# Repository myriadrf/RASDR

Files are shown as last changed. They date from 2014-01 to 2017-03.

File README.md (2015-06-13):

# Radio Astronomy Software Defined Receiver (RASDR)

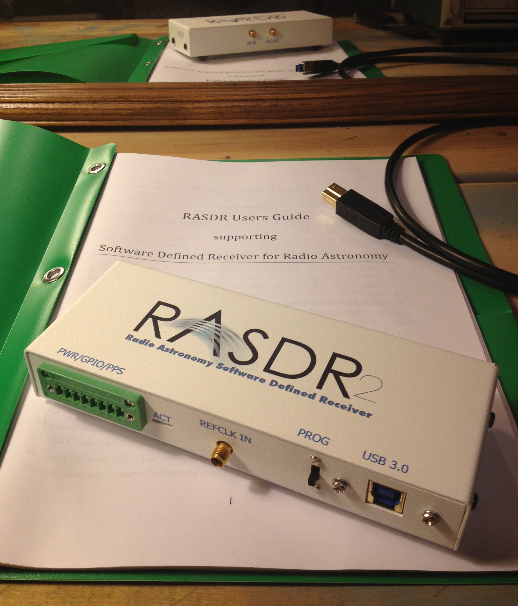
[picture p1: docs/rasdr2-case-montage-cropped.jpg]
RASDR


This project provides access to the hardware designs, firmware, host system drivers and applications for the RASDR project.  RASDR is an Open Hardware project undertaken by members of the Society of Amateur Radio Astronomers (SARA) to develop a low cost, high performance software defined receiver for use by SARA members.  The goal of RASDR is to provide a low cost hardware that enables radio astronomers and educational institutions to perform high quality astronomical measurements.

At the core of this capability is the Lime Microsystems, Ltd. LMS6002D Field Programmable Radio Frequency device.  The device supports tunable RF reception over a wide range (400MHz to 3.8GHz) and high bandwidth (28Mhz).  Through the use of a Host Interface Module, the LMS6002D is connected to a personal computer (PC) over a standard USB link.  Both USB3 and USB2 are supported to enable the widest possible field of use, although full bandwidth of the LMS6002D is only achieved when using USB3.

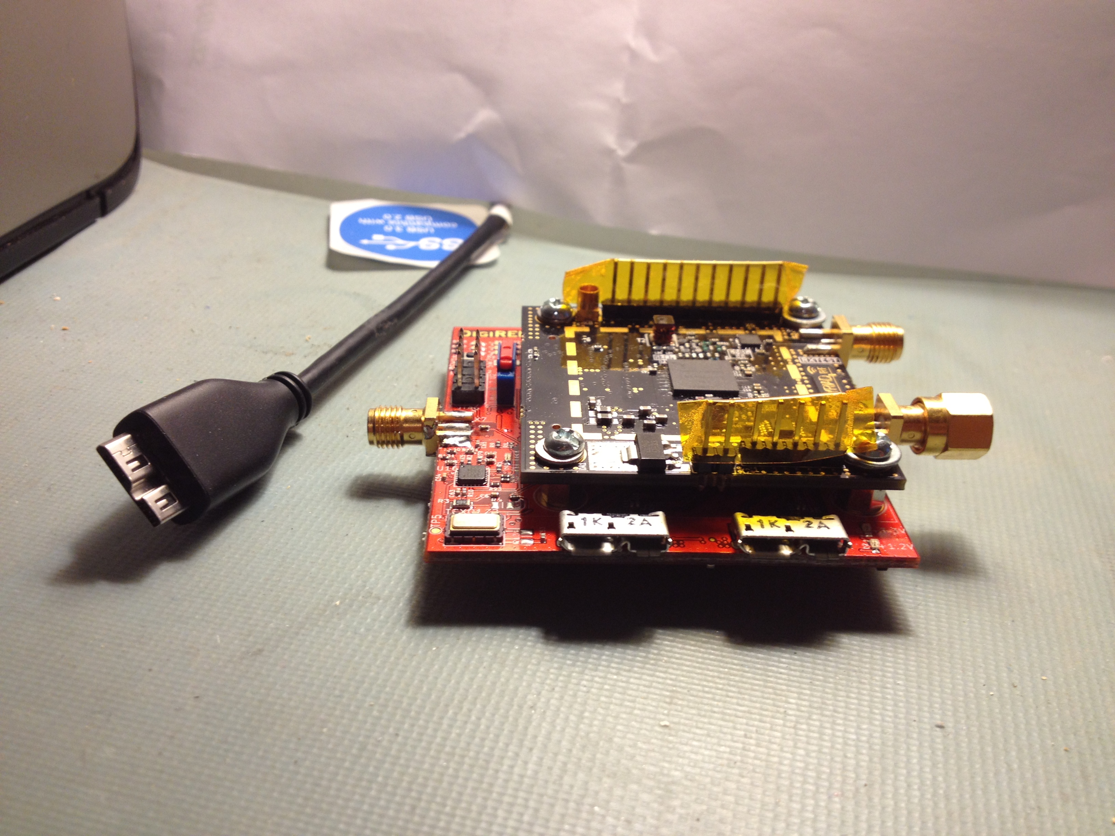
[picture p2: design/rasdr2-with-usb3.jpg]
RASDR-COMPONENTS

*RASDR2 hardware components consisting of DigiRED and MyriadRF modules*

## Device Specifications ##

Radio Astronomy research is dominated by sensitive front-end radio detection and amplification equipment, a wide-bandwidth analog to digital conversion stage, and finally, a digital processing system to extract and present information.  RASDR hardware is designed to provide all these functions in a low size, weight, and power form-factor.

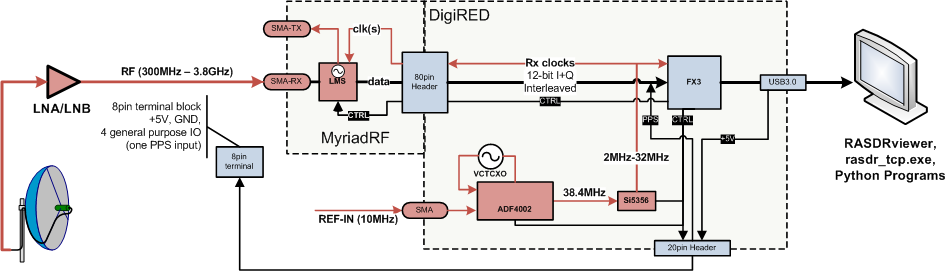
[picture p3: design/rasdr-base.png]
RASDR-DIAGRAM

*RASDR2 block diagram showing basic use case and components*

One RF transceiver chip provides receive functionality.  The transmit section is calibrated to produce a continuous wave (CW) tone that is useful for up/down conversion of signals into the tuning band of the receive section.  Wideband SMA connectors are available to enable reception in the region between 300 MHz to 3.8 GHz with up to 28 MHz of bandwidth at 12 bit I/Q sampling.  The RASDR designs and driver source code are freely available at the RASDR Open Source project, please visit [MyriadRF.org](https://myriadrf.org/) for details.

### Features ###

- Two channel simultaneous receive at max. 28 MHz bandwidth (transmit functions disabled in factory firmware and logic)
- Lime Microsystems, Ltd. FPRF transceiver programmable between 300 MHz to 3.8GHz with 12 bit I/Q sampling and 9 built-in RF Paths.
- Maximum Data Transfer of 160MB/s
- External reference clock input, enabling synchronous operation with test equipment and facility timing signals
- External general purpose I/O (GPIO) port providing 4 3.3V GPIOs and +5V power (1.25W maximum)
- Pulse Per Second (PPS) input on GPIO synchronously sampled and available in the receive data stream
- Power: +5V USB @ 0.75A (3.75W maximum required power)

### Electrical Interface ###

- SuperSpeed USB3 or USB2 data and power.  Max data rates: 160MB/s or 35MB/s respectively.
- SMA receive input, 50ohm, 300MHz to 3.8GHz
- SMA reference input, 50ohm, 10MHz
- SMA transmit output, 50ohm, 300MHz to 3.8GHz

### Physical Specifications ###

- Size:  165mm x 70mm x 32mm (6.5" x 2.75" x 1.25")
- Weight: approx. 653 gram (1lb 7oz.)

## Directory Description ##

- **design** � directory contains high-level design documents and specifications for the RASDR2 module and host APIs. This directory also includes development and testing information.

- **DigiRED** � contains the hardware design files, firmware and information needed to manufacture the various host interfaces modules.  The embedded firmware for the FX3 provides the SuperSpeed USB 3.0 interface and can also be customized for conditional on board processing within the limits of the internal RAM.

- **rfmodule** � contains the hardware design files and information needed to manufacture the MyriadRF module that sits atop the DigiRED.

- **host** � the host directory contains host processor APIs, device drivers and libraries for accessing the RASDR modules via USB. Support is provided for embedded C/C++ development.

## Licensing ##
Unless otherwise specified, all software source files are licensed using the GNU General Public license version 2.  All hardware related designs and source artifacts are licensed under the  �Creative Commons Attribution 3.0 Unported�. To read the details of the license please review "license.html" or visit http://creativecommons.org/licenses/by/3.0/legalcode.

For specific information see the COPYING.MD file(s).

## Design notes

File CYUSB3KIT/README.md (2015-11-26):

# CYPRESS USB 3.0 SuperSpeed Explorer Kit

A Cypress FX3-based interface with general purpose connectivity.

## Contents

This folder contains projects used in debugging RASDR components using the Cypress SuperSpeed Explorer Kit.  This is an inexpensive development board distributed by Cypress Semiconductor, Ltd.

CYUSB3KIT

The hardware can be ordered directly from Cypress; see the information page [here](http://www.cypress.com/documentation/development-kitsboards/cyusb3kit-003-ez-usb-fx3-superspeed-explorer-kit).

## Software

The 'streamer' folder contains a modified version of the Cypress streamer example program that is distributed in the [EZ-USB FX3 Software Development Kit](http://www.cypress.com/documentation/software-and-drivers/ez-usb-fx3-software-development-kit).  It has been updated to compile in Microsoft Visual Studio 2013 Express, to compile outside of the FX3 installation folder, and to allow a queue size of up to 512 transfers.

## Firmware

The 'ssek_emu' folder contains a firmware that is a modified version of the SS Explorer Kit project 'USBBulkSourceSinkLED' .  It has been modified to respond to the RASDR Vendor Command Set, and identify itself as a compatible RASDR device.  The firmware produces representative I/Q data of 'noise' in a replay-buffer manner, at approximately the same rate as a real RASDR device would

The firmware can be loaded to the CYUSB3Kit board by fitting the PMODE jumper J4, resetting the device, and using the CyControl program provided by the RASDR distribution to load the 'ssek_emu.img' to RAM.

To install the firmware into the I2C EEPROM, simply load the 'ssek_emu.img' to I2C.  Upon removing the PMODE jumper and resetting the CYUSB3KIT, the device will function as a RASDR emulator.

## Driver

Use the driver provide by the RASDR distribution for the above firmware(s).  Using the above firmware with the CYUSB3KIT will identify itself as a DigiRED_EMU device.

## Acknowledgement

The RASDR developers wish to thank Cypress Semiconductor, Ltd. for producing the SuperSpeed Explorer Kit, its resulting firmware files.  Inspecting these files has been instrumental in repairing a few long-standing deficiencies in the behavior of RASDR devices and USB3.0.

In addition, the availability of the Kit enables would-be RASDR users to obtain hardware and begin to explore the use of the RASDRviewer and other softwares in advance of obtaining an actual RASDR device which are currently circulating in a loaner program for [Society of Amateur Radio Astronomers](http://www.radio-astronomy.org/) members.

## Licensing

### Software

For details of software licensing please see the associated license.txt files in each folder.

### Firmware

For details of firmware licensing please see the associated license.txt or COPYING file(s) in each folder.

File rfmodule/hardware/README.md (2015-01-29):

# Myriad-RF 1 RF Module version 1

## IMPORTANT!

Previous versions are retained for reference and are not intended for use in manufacturing.

## Changes

Note that r1 and r2 were interim updates and were not manufactured.

### 2014-03-03 r.3

Updated due to obsolete components.

Changed:

#### Schematics updates, pages "Clocks” and  “RF FE":

1. Component DA6 - Obsolete RF switch (PE4210) is changed, to new part PE42422
2. Added capacitor on TX Test track C26=100pF

#### PCB Layout updates

1. New footprint of PE42422 part
2. Rounded RF tracks
3. The GND and power supply vias mask closed (so there is no open vias on board)
4. The board annotation note "Board v.1 r.3" on the bottom layer silkscreen
5. The dimension lines (48 x 46 mm) on Drawings layer

#### BOM updates

1. Manufacturer of the capacitors is to KEMET: Capacitor values: 1.2pF, 1.8pF and 3.9pF
2. Included Board revision line
3. Changed dimensions to 48 x 46 mm
4. Included Drawings layout in list of gerber files
5. Included more report files in report folder

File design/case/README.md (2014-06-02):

# RASDR Case Design Tools

This sub-project generates a case model and manufacturing files for the RASDR project.  RASDR is an Open Hardware project undertaken by members of the Society of Amateur Radio Astronomers (SARA) to develop a low cost, high performance software defined receiver for use by SARA members.  The goal of RASDR is to provide a low cost hardware that enables radio astronomers and educational institutions to perform high quality astronomical measurements.

At the core of this capability is the Object Oriented Mechanics Library ([OOML](http://iearobotics.com/oomlwiki/doku.php)), which is used by the [OOML Case Factory](http://www.thingiverse.com/thing:70838) and custom code to produce the CAD files that are used to generate the STereoLithograpy (STL) files needed to produce a design.

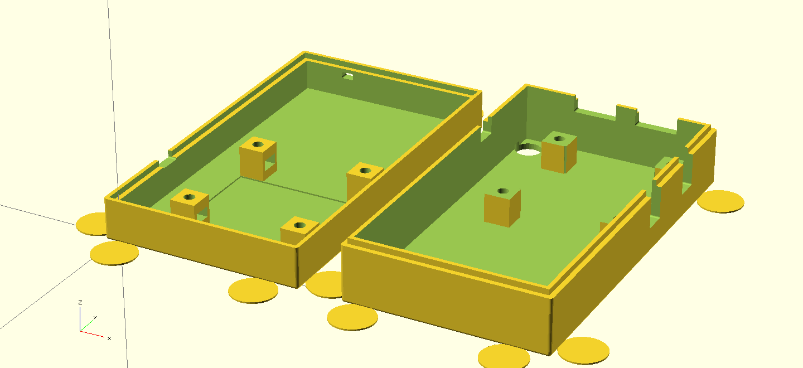
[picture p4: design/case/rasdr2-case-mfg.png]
RASDR

*RASDR2 case design generated using the OOML Case Factory with manufacturing aids*

## Setup of the Tools ##

You will need to setup the OOML and OpenSCAD on your machine.  Here are links:
- [OOML](http://iearobotics.com/oomlwiki/doku.php?id=download:start)
- [OpenSCAD](http://www.openscad.org/)

Forgive me if at this point, I don't have a step-by-step for all platforms.  The above links do a good job.  If you have problems, please send me an email and I'll try to help you out.

## Regenerating the Design ##

Once you have done that, just edit the Makefile to help it find the install location of the library (not needed if you installed into /usr/include/ooml)

Then, simply issue the following commands:

- $ make
- $ ./casefactory

This will produce (at least) the following files:

rasdr-case-bottom.scad
rasdr-case-top.scad
rasdr-case-mfg.scad

The first two are the individual top/bottom parts of the case.  The third is a "manufacturing" version of the case that contains *both* top and bottom parts, as well as 'rafts' to help keep the surfaces from curling.

## Viewing the Design ##

At this point, start OpenSCAD and open one of the above .scad files.  The tool will construct the rendering and you can use the tool to inspect the model from all perspectives, rotate, pan, zoom, etc.

Each time you run the above two commands, you will update the .scad files and OpenSCAD will refresh its rendering.  When you are ready to print the case, you *export* an STL file and send that to your slicer and *happy printing*.

## Licensing ##
These software source files are licensed using the *GNU General Public license version 3*.  This is because the OOML Case Factory is released under this license model.
For specific information see the LICENSE file.

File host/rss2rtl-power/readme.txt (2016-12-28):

Usage: rss2rtl-power.py [options]

 Script to emulate a Radio Sky Spectrograph client application to capture
spectrograph output from a streaming server and write it in an ASCII .csv
format as described by rtl-power.  Two stream protocols are offered: Basic
Radio Sky Spectrograph(http://cygnusa.blogspot.com/2015/07/how-to-talk-to-
radio-sky-spectrograph.html) Binary rtl-power/Extended RSS
Spectrograph(https://github.com/myriadrf/RASDR/issues/16)

Options:
  --version          show program's version number and exit
  -h, --help         show this help message and exit
  -a A, --address=A  Specify the server address; default=localhost
  -p N, --port=N     Specify the port to connect to; default=8888
  -i, --info         Produce information about the connection only; do not
                     receive/parse scans
  -e, --extended     Interpret the extended RSS format
  --iso8601          Emit ISO-8601 Timestamps (YYYY-MM-DDTHH:MM:SS.nnnZ),
                     default=False
  --statistics       Dump statistical information to the stderr in comma-
                     separated-values format, default=False
  -v, --verbose      Verbose
  -q, --quiet        Do not display a connection message on stderr

Examples:

dos> rss2rtl-power.exe > standard.csv

This will start the client, connect to localhost:8888, emit the connection
string and begin reading 'standard' RSS protocol.  It will perform a local
timestamp and write the results to the file standard.csv.

dos> rss2rtl-power.exe -e --statistics > extended.csv

This will start the client, connect to localhost:8888, emit the connection
string and begin reading the 'extended' RSS protocol.  This protocol provides
the timestamp in the packet header and higher precision on the power spectral
density output.  Statistics will be calculated and emitted on the stderr while
the program runs (not in the output file).  The results will be written to the
file 'extended.csv'.

Notes:

The 'standard' RSS protocol is described here:
http://cygnusa.blogspot.com/2015/07/how-to-talk-to-radio-sky-spectrograph.html

The 'extended' RSS protocol is described here:
https://github.com/myriadrf/RASDR/issues/16

If you have python installed, you can also run the program with the python interpreter:

dos> python rss2rtl-power.py > output.csv

Should produce the same result as using the pre-compiled program.

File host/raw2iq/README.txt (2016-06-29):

Convert RASDRstreamer raw stream into a I/Q output

Usage:
dist\x86\raw2iq.exe [OPTIONS]
Where:
  -i, --input-file FILE   Full path to file to be read or - for stdin
  -o, --output-file FILE  Full path to file to be written or - for stdout
  --iq-polarity N         Define starting I/Q polarity level
                            (0=I sample first, 1=Q sample first, default=0)
  --pps-polarity N        Define OTM/PPS polarity level
                            (0=active low, 1=active high, default=0)
  --flag-value HEX        Define FLAGs code for valid data
                            (two bits, default=3)
  --flag-mask HEX         Define FLAGs mask (two bits, default=3)
  -v                      Increment verbosity level
  --verbose N             Define verbosity level (0=quiet, 1=info, 2=trace)
  -h, --help              Print this help

Examples:

dist\x86\raw2iq.exe < RASDRviewer.raw > test.dat
Converts the .raw file to a binary interleaved 16-bit signed I/Q format file.

dist\x86\raw2iq.exe < RASDRviewer.raw -o test.csv
Converts the .raw file to an ASCII 16-bit signed I/Q comma separated file.

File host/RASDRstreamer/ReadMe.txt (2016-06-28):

==============================================================================
    APPLICATION : RASDRstreamer Project
==============================================================================

This project is derived from the CYPRESS FX3 Development Kit project, "C++ Streamer".  It can be used to collect RAW data from a RASDR device.

The Cypress program, "C++ Streamer" was useful for evaluating USB2/USB3 performance of the FX3 chips.  The original program source is provided at:
"C:\Program Files\Cypress\EZ-USB FX3 SDK\1.3\application\cpp\streamer"

I have updated the program to compile with Microsoft Visual Studio Express 2013 for Windows Desktop, to accept the RASDR VID/PID and to build for X86 and X64 windows archicectures.  Additionally, I have added the ability for it to write data out to a file.  The source code to the program is provided at:
https://github.com/myriadrf/RASDR/tree/master/host/RASDRstreamer

To use the Program, perform the following steps:

1) insert RASDR device to a USB2 or USB3 port
2) Load RASDRviewer 1.2.2.2 or RASDRproc, and configure it to the acquisition parameters you wish to use.  { sample rate, samples/frame, bandwidth, gain settings, etc. }
   a. Please note that when using USB2, 10 MS/s is the practical limit
3) Ensure that you are taking data the way you want it by using RASDRviewer to START and STOP capturing samples.
4) Start RASDRstreamer.exe (x86 or x64) and select the RASDR device in the Connected Devices List
   a. This may either be "(0x1D50 - 0x6099) RASDR Radio Astronomy SDR..."
   b. Or it may be "(0x04B4 - 0x00F1) Cypress FX3 USB StreamerExample..." (if you are using the CYFX3KIT hardware for testing)
   c. Select the "BULK IN ..." Endpoint
5) Select the 'Samples/Frame', 'Rate (MHz)' and 'Integration Time (ms)' fields to match what RASDRviewer was set to.
   a. These settings only define the packetization parameters, the actual transfer rate was defind by the RASDRviewer configuration of the LMS6002D chip.
6) Decide you wish to save RAW data or not by ticking the check box
   a. When using USB3 and writing .raw file, you will observe a rate reduction when the in-memory file system buffers fill up.
7) Press START.

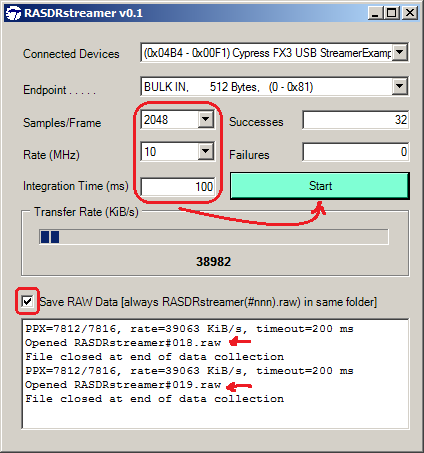
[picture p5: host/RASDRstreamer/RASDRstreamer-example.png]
RASDRstreamer-example

*RASDRstreamer GUI showing steps 4-7 and example progress output*

You will observe successful packets accumulating, the actual transfer rate in KiB/s reported in the GUI.  In the text box below the transfer rate, you will see the packetization parameter and the expected transfer rate based on the selection above.  If you chose to save RAW data, it will also tell you the filename it chose to use.

The program does not overwrite an existing file, rather it adds a '#NNN' suffix to create a unique filename each time.  The files will always have the form 'RASDRstreamer#NNN.raw' as described in the GUI and will always be in the location in the filesystem that the .exe is started from [as of v0.1].

The format of the data are interleaved I and Q 16-bit samples encoded as described in Appendix E of the RASDR User Manual pg. 67-68.  That is, the control bits for I/Q, FIFO flags and PPS are encoded and must be removed in post-processing to interpret the ADC data.  The I/Q streams will also need to be de-interleaved and aligned.  If the HOST PC data acquisition system cannot keep up with the actual data rate (as calculated) then correct interpretation of the I/Q data may require flipping of bits and re-synchronizing to the PPS signal bit.

NOTE:  As per Microsofts documentation:
https://msdn.microsoft.com/en-us/windows-drivers/develop/using_the_microsoft_c_runtime_with_user_mode_drivers_and_apps

The VC re-distributable components are provided with the application file.  They can also be downloaded here:
https://www.microsoft.com/en-us/download/details.aspx?id=40784

==============================================================================
    BUGS
==============================================================================

1) RASDR2 Firmware prior to June 2016 (Device Descriptor BcdDevice="00 03" or earlier) had issues with USB3 operation on certain computers (lower specification) that caused glitches and failed transports.  With Firmware BcdDevice="00 04", this has been *partially mitigated* by eliminating the burst mode when using USB3 SuperSpeed mode.  The change does not eliminate the glitch, but reduces its liklihood considerably.

The workaround is a software close and re-open of the USB device.  For RASDRstreamer, this can be accomplished by restarting the program or stopping the transfer and re-selecting the device, then pressing START.  With version v0.2.1 and later, the program has a compile-time choice to perform a self-restart and continue acquiring buffers.  This seems to work until the firmware gets into a non-recoverable state (see #3) below, which then requires a disconnect/reconnect cycle.

2) v0.1.2 and below of RASDRstreamer has a threading issue in the ::Display() call that leads to random exceptions.  Particularly if there is an early failure in the USB immediately upon pressing the START button.

3) If you get 'Xfer request rejected. NTSTATUS = c0000001' when trying to START, this means that the firmware has entered an invalid state, and the device must be disconnected and reconnected.  (The Firmware BcdDevice="00 04" is only *partially mitigated*) 
 
==============================================================================
    CHANGELOG
==============================================================================

v0.2.2 - Bugfix

  Add workaround for NULL endpoint at Start
  Fix bug that caused Device selection to be left disabled upon a failure at start.

v0.2.1 - First release with restart capability

  Add (configurable) code to re-initialize the USB device when a transfer failure is detected
  Refactor management of the USBDevice and EndPt pointer to reduce interdependent references
  (some whitespace changes due to the microsoft editor)

v0.2.0 - Unreleased

  Refactor buffers in XferLoop() to be conducive to restart operation
  Keep success/failure count persistent across XferLoop() starts/stops

v0.1.3 - Unreleased

  Add queued string output to prevent crashes
  Add temporary workaround 'CheckForIllegalCrossThreadCalls=false' for calling UI components from thread functions

<rant>Why does *every* example software have such bad UI thread issues?  Its crushing how much code is written like this.  It works for simple cases, and then as soon as you start to extend it...  boom, crash, game over.  Its such a waste of time.  You were much better off starting from scratch.  But then...  you will have invested so much time in the code that any rational human being will want to get some compensation for it, and you will close the source and keep it secret.  Well, I am not rational, so I hope that my (insignificant) efforts at repairing these will help some poor soul stuck with the same problems in the code they have to deal with.</rant>

v0.1.2 - Unreleased

  Add vertical scrollbar to diagnostic output
  Fix bug not using 'rb' when writing .raw files that leads to files getting premature EOF

v0.1.1 - First Public Distribution

  Track when transfer rate is not close to what is expected
  Color the transfer rate bar if the expected/actual data rate differs by more than 3% and 10%
  Fix bug when closing if raw output file is not opened

v0.1 - First Source Code Release

  Evaluates expected/actual data rate received, handles (recoverable) USB3 glitches gracefully.  Saves .raw files not overwriting the previous sequence number if it exists.

==============================================================================
    FILE SUMMARY
==============================================================================

This is a summary of what you will find in each of the files that make up the Streams application which uses cypress C++ library CyAPI.lib.

RASDRstreamer.vcproj/.vcxproj
    This is the main project file for VC++ projects generated using an Application Wizard. 
    It contains information about the version of Visual C++ that generated the file, and 
    information about the platforms, configurations, and project features selected with the
    Application Wizard.

RASDRstreamer.cpp
    This is the main application source file (boilerplate).

RASDRstreamer.h
    Contains the implementation of the program, according to .NET style.

AssemblyInfo.cpp
    Contains custom attributes for modifying assembly metadata.

Other standard files:

StdAfx.h, StdAfx.cpp
    These files are used to build a precompiled header (PCH) file
    named Win32.pch and a precompiled types file named StdAfx.obj.

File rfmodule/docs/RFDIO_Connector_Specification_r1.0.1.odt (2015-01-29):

RFDIO Connector

Specification

v1.0

Copyright 2014 Lime Microsystems Ltd

CC BY 3.0

Contents

Table of Figures

Figure 1. RFDIO connectors 3

Figure 2. Recommended PCB footprint 5

Figure 3. MyriadRF card mechanical coordinates (Top view) 5

The information contained in this document is subject to change without prior notice. No responsibility for its use, nor for infringement of patents or other rights of third parties is assumed.

The information contained in this document is subject to change without prior notice. No responsibility for its use, nor for infringement of patents or other rights of third parties is assumed.

# General Description

The Myriad-RF Radio Frequency Digital Input Output (RFDIO) connector specification defines the electrical and mechanical properties of a high speed card interface for Field Programmable Gate Array (FPGA) based carrier boards. This specification ensures interoperability between carrier (mother) boards and add-on (daughter) RF cards.

The connector is designed to meet the IEEE802.3ap backplane link to meet 10G Ethernet compliant signal channels.

# Mechanical Specifications

The connector is based on the Hirose 0.5 mm pitch, 80 positions, surface-mount connector. The part numbers are:

The female part number is FX10A-80S/8-SV, to be assembled on the motherboard. The male part number is FX10A-80P/8-SV1, and is to be used by the daughterboard. A typical example of use for an RF application is an Altera FPGA motherboard, using a Myriad-RF daughterboard. This example with be used in the document for clarity.

Figure 1 shows the connectors in 3-D view.

Figure 1. RFDIO connectors

Figure 2 shows the recommended land pattern (Metal Mask) connector dimensions.

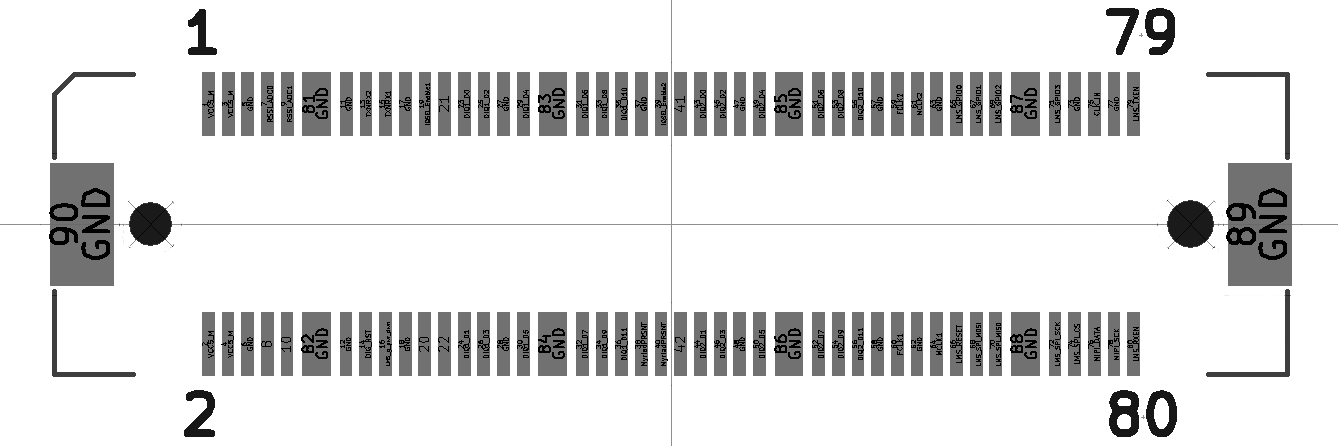
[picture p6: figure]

1.6

0.3

0.7

0.5

0.75

3.05

3.1

1.6

13.2

14.95

1.1 NPTH

1.2 NPTH

Figure 2. Recommended PCB footprint

A footprint for the open source EDA software, KiCad, is available via the database provided by the Myriad-RF Component Libraries project (https://myriadrf.org/projects/component-libraries/).

Figure 3 shows the dimensions of the Myriad-RF 1 daughterboard with the Hirose connector.

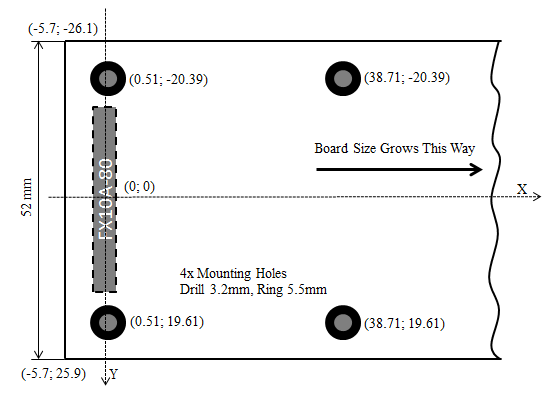
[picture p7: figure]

Figure 3. Myriad-RF card mechanical coordinates (Top view)

# Electrical Specifications

## Power

The carrier board must provide +5V (1.5A) DC to the RF card through the RFDIO connector. The maximum current via the Hirose connector is 0.3A per pin. To achieve the 1.5A specification, a number of defined supply and ground pins must be used. These are:

+5V: Pin 1, 2, 3, 4, 8 & 10.

GND: Pin 5, 6, 11, 12, 17, 18, 27, 28, 37, 38, 47, 48, 57, 58, 62, 63, 73, 77, 81, 82, 83, 84, 85, 86, 87, 88, 89 & 90

## CMOS Signals

The CMOS class pins are intended to connect directly to pins that support LVTTL compatible single-ended I/O standards such as 3.3-V LVTTL/LVCMOS or 2.5-V LVTTL/LVCMOS.

All CMOS class pins must support bidirectional operation.

Signals between the host FPGA device and HSMC connector are intended to be D/C coupled.

## Bus Widths

Daughterboards must be designed to support the full specified bus widths. This will guarantee interoperability with the greatest number of RF cards.

## Termination

Tracks must have 50 Ω single-ended impedances. An optimum design will be obtained if the host FPGA supports driver strength control where 50 Ω output impedances can be selected. This output impedance will match the characteristic impedance of the tracks themselves. For long track lengths or heavy loads, drive strength may be increased as necessary until optimal signal integrity is achieved for the specific carrier board or RF card combination. When impedance control is not possible, it is recommended to place series resistors on each line of the host board to allow for tuning through resistor value changes. Default resistors should be a nominal 0 Ω since signal direction cannot be assumed on a carrier board and higher value resistors found near a receiver can significantly degrade signal integrity.

## Pinout

The RFDIO connector has a total of 90 pins, including 54 digital signals pins, 6 power pins, 2 analog pins and 28 ground pins.

Table 1 (Part 1 of 2). RFDIO connector’s pinout

Pin Nr | Function | Description | Pin Nr | Function | Description
1 | 5V | Power | 2 | 5V | Power
3 | 5V | Power | 4 | 5V | Power
5 | GND | Power | 6 | GND | Power
7 | RSSI output | analog | 8 | 5V | Power
9 | RSSI output | analog | 10 | 5V | Power
81 | GND | Power | 82 | GND | Power
11 | GND | Power | 12 | GND | Power
13 | TXNRX2 | CMOS IN | 14 | GPIO5 | CMOS IO
15 | TXNRX1 | CMOS IN | 16 | G_PWR_DWN | CMOS IN
17 | GND | Power | 18 | GND | Power
19 | ENABLE_IQSEL1 | CMOS IN | 20 | GPIO6 | CMOS IO
21 | SPI_EN_BRD | CMOS IN | 22 | GPIO7 | CMOS IO
23 | DIQ1_D0 | CMOS IO | 24 | DIQ1_D1 | CMOS IO
25 | DIQ1_D2 | CMOS IO | 26 | DIQ1_D3 | CMOS IO
27 | GND | Power | 28 | GND | Power
29 | DIQ1_D4 | CMOS IO | 30 | DIQ1_D5 | CMOS IO
83 | GND | Power | 84 | GND | Power
31 | DIQ1_D6 | CMOS IO | 32 | DIQ1_D7 | CMOS IO
33 | DIQ1_D8 | CMOS IO | 34 | DIQ1_D9 | CMOS IO
35 | DIQ1_D10 | CMOS IO | 36 | DIQ1_D11 | CMOS IO
37 | GND | Power | 38 | GND | Power
39 | ENABLE_IQSEL2 | CMOS IN | 40 | BRDPRSNT | Board present, connects to GND on RF card
41 | GPIO4 | CMOS IO | 42 | VIO | Digital IOs supply
43 | DIQ2_D0 | CMOS IO | 44 | DIQ2_D1 | CMOS IO
45 | DIQ2_D2 | CMOS IO | 46 | DIQ2_D3 | CMOS IO
47 | GND | Power | 48 | GND | Power
49 | DIQ2_D4 | CMOS IO | 50 | DIQ2_D5 | CMOS IO
85 | GND | Power | 86 | GND | Power
51 | DIQ2_D6 | CMOS IO | 52 | DIQ2_D7 | CMOS IO
53 | DIQ2_D8 | CMOS IO | 54 | DIQ2_D9 | CMOS IO
55 | DIQ2_D10 | CMOS IO | 56 | DIQ2_D11 | CMOS IO
Table 1 (Part 2 of 2). RFDIO connector’s pinout
Pin Nr | Function | Description | Pin Nr | Function | Description
57 | GND | Power | 58 | GND | Power
59 | FCLK2 | CMOS CLK in | 60 | FCLK1 | CMOS CLK in
61 | MCLK2 | CMOS CLK out | 62 | GND | Power
63 | GND | Power | 64 | MCLK1 | CMOS CLK out
65 | GPIO0 | CMOS IN | 66 | RESET | CMOS IN
67 | GPIO1 | CMOS IN | 68 | SPI_MOSI | CMOS IN
69 | GPIO2 | CMOS IN | 70 | SPI_MISO | CMOS OUT
87 | GND | Power | 88 | GND | Power
71 | GPIO3 | CMOS IN | 72 | SPI_CLK | CMOS IN
73 | GND | Power | 74 | SPI_EN_LMS | CMOS IN
75 | CLK_IN | CMOS Reference CLK input for RF card | 76 | MIPI_SDA | CMOS IO
77 | GND | Power | 78 | MIPI_SCL | CMOS IN
79 | TXEN | CMOS IN | 80 | RXEN | CMOS IN
89 | GND | Power | 90 | GND | Power

*for complete signals description and timing diagrams refer to LMS6002D (http://www.limemicro.com/download/LMS6002Dr2-DataSheet-1.2r0.pdf) or LMS7002M (http://www.limemicro.com/download/LMS7002M-DataSheet%202.0r1%20Preliminary.pdf) datasheet

Myriad-RFRFDIO Connector Specification

Rev: 1.0.1 The information contained in this document is subject to change without prior notice. No responsibility for its use, nor for infringement of patents or other rights of third parties is assumed. Rev: 1.0.1 Last modified: 12/16/2014 The information contained in this document is subject to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

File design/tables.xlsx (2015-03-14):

DigiRED R50,52,56 | MyriadRF R95 | SPI_SSN_Rx pullup | SPI_SSN_Rx pulldn | Jumper on J2 (RX) | Press SW2 (RX) | Power On | Boot Behavior | Voltage at R115 | Current thru R115 | Notes
YES | YES | N/C | N/C | NO | X | X | Bootloader | N/A | N/A
YES | YES | N/C | N/C | YES | YES | NO | Bootloader | N/A | N/A
YES | YES | N/C | N/C | YES | NO | YES | Load SPI Flash Program | N/A | N/A
YES | NO | N/C | N/C | NO | X | X | Bootloader | N/A | N/A
YES | NO | N/C | N/C | YES | YES | NO | Bootloader | N/A | N/A
YES | NO | N/C | N/C | YES | NO | YES | Bootloader | N/A | N/A
NO | N/C | N/C | N/C | NO | X | X | Bootloader | N/A | N/A | MyriadRF board is not attached
NO | N/C | N/C | N/C | YES | YES | NO | Load SPI Flash Program | N/A | N/A | MyriadRF board is not attached
NO | N/C | N/C | N/C | YES | NO | YES | Load SPI Flash Program | N/A | N/A | MyriadRF board is not attached
NO | NO | N/C | N/C | X | X | X | Bootloader | N/A | N/A
NO | NO | 100 ohm | NO | YES | NO | YES | Bootloader | 3.29V | 0 mA
NO | NO | 100 ohm | NO | YES | YES | NO | Bootloader | 3.29V | 0 mA
NO | NO | NO | 100 ohm | YES | NO | YES | Load SPI Flash Program | 2.7V | 27 mA
NO | NO | NO | 100 ohm | YES | YES | NO | Bootloader | 0.0V | 0 mA
NO | NO | NO | NO | YES | NO | YES | Bootloader | 2.6V | N/A
NO | NO | NO | NO | YES | YES | NO | Bootloader | 2.6V | N/A
NO | NO | 2.2K ohm | NO | YES | NO | YES | Bootloader | 3.29V | 0 mA
NO | NO | 2.2K ohm | NO | YES | YES | NO | Bootloader | 3.29V | 0 mA
NO | NO | NO | 2.2K ohm | YES | NO | YES | Load SPI Flash Program | 3.26V | 1.5 mA
NO | NO | NO | 2.2K ohm | YES | YES | NO | Bootloader | 0.1V | 45 uA
NO | N/C | 2.2K ohm | NO | YES | NO | YES | Load SPI Flash Program | 3.29V | 0 mA | MyriadRF board is not attached
NO | N/C | 2.2K ohm | NO | YES | YES | NO | Load SPI Flash Program | 3.29V | 0 mA | MyriadRF board is not attached
NO | N/C | NO | 2.2K ohm | YES | NO | YES | Load SPI Flash Program | 3.26V | 1.5 mA | MyriadRF board is not attached
NO | N/C | NO | 2.2K ohm | YES | YES | NO | Load SPI Flash Program | 3.26V | 1.5 mA | MyriadRF board is not attached

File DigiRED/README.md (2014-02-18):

# DigiRED USB 3.0 Interface Module 

A Cypress FX3-based interface for the Myriad-RF 1 module.

## Contents

### Hardware design

The directory structure for the hardware design is as follows:

      hardware/<version>/
          BOM/                   - bill of materials spreadsheet
          Gerbers/               - Gerber CAM files
          KiCAD/                 - KiCAD schematic and layout files
          Manufacturing/         - Additional manufacturing information
          PDF/                   - Schematic and layout PDFs
          Reports/               - DRC, ERC and drill reports

## Firmware

FX3 controller firmware.

      firmware/
          bin/                   - binary releases
          src/                   - source code

## Driver

Windows drivers for the DigiRED Module

      driver/
          digired-windows.zip    - Windows Drivers for DigiRED

## Licensing

### Hardware

The hardware design is licensed under a Creative Commons Attribution 3.0 Unported licence.

### Firmware

For details of firmware licensing please see the associated COPYING file(s).

### Driver

For details of driver files licensing please see the license.txt in the driver/

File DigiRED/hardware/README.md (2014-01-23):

## DigiRED Hardware Designs ##
This directory contains the hardware source artifacts for the DigiRED host interface module.  

## Directory Structure ##
The directory is organized into the various published hardware revisions: v1r3(prototype), etc...

----------

## Designs / Source Artifacts Licensing ##
All hardware source artifacts contained within this directory are licensed under the “Creative Commons Attribution 3.0 Unported”.  To read the details of the license please review "COPYING" or visit [http://creativecommons.org/licenses/by/3.0/legalcode.](http://creativecommons.org/licenses/by/3.0/legalcode.)

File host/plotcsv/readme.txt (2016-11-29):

usage: plotcsv.py [-h] [--version] [-v | -q] [-a N] [-b PATH] [-c] [-d CHAR]
                  [-e] [-k CONST] [-l] [-i] [--statistics PATH] [--debug] [-g]
                  [-s N] [--fcenter FC] [--hold] [--bplot] [--ptype TYPE]
                  [--atype TYPE] [--format X.Y.Z]
                  [file [file ...]]

Post-Process RASDRviewer/RASDRproc spectrum data output files

positional arguments:
  file

optional arguments:
  -h, --help            show this help message and exit
  --version             show program's version number and exit
  -v, --verbose         Turn on verbose output
  -q, --quiet           Suppress progress messages
  -a N, --average N     Specify the number of spectra to average for each plot
  -b PATH, --background PATH
                        Specify how to perform background subtraction;if the
                        word automatic is used, then the background will be
                        takenfrom the average of all lines in the file.
                        Otherwise, it is takenas a file to process. The file
                        must have the same frequency plan as the foreground
                        file.
  -c, --cancel-dc       Cancel out component at frequency bin for 0Hz
  -d CHAR, --delimiter CHAR
                        Specify the delimiter character to use"
  -e, --localtime       Indicate that .csv file has timestamps in
                        RASDRviewer's "LocalTime" format
  -k CONST, --calibration CONST
                        Specify the calibration constant for the system;
                        0.0=uncal
  -l, --line            Perform line-by-line processing instead of loading
                        entire file(s); NOTE: much slower but tolerates low
                        memory better.
  -i, --info            Produce information about a file only; do not generate
                        any plots
  --statistics PATH     Dump statistical information to a file in comma-
                        separated-values format
  --debug               Drop into ipython shell at predefined point(s) to
                        debug the script
  -g, --gui             Create interactive PLOTS
  -s N, --smooth N      Smooth final plot using a sliding window of N points
  --fcenter FC          Define the offset for the center frequency in Hz
  --hold                Perform a maximum value HOLD during averaging and plot
                        it as a second line
  --bplot               If using background file, choose whether to plot the
                        background reference in a difffert color
  --ptype TYPE          Control plot vertical scale (linear or log)
  --atype TYPE          Control averaging method (linear or log)
  --format X.Y.Z        Specify the RASDRviewer .csv output format to
                        interpret

NOTES:

Edit the 'go.bat' provided to assign the path to the file and any needed options.  Then double-click the go.bat file.

If you have python installed, you can also run the program with the python interpreter:

dos> python plotcsv.py FFTOut-2msps-500avg-srh77ca.csv -a 120

Should produce the same result as using the pre-compiled program.

Several versions of RASDRviewer had produced different header formats that
need to be parsed differently.  The --format option allows you to specify
this if you are dealing with older data files.  Currently valid options are:
1.0.4, 1.1.1, 1.2.2 (current)

The file 'environment.yml' provides an easy way to generate a python virtual environment that has the needed dependencies.  Using Anaconda, execute:

$ conda env create -f environment.yml
$ source activate rasdr
-or-
dos> activate rasdr

See: https://docs.continuum.io/anaconda/install.html
See also: http://conda.pydata.org/docs/using/envs.html#use-environment-from-file

BUGS:

1) the cancel DC option isnt effective as it seems the highest energy is 2 bins away from actual Frequency 0
2) The file formats need to be described
3) The 'append' feature in RASDRviewer that adds a new frequency header to the same file is not supported correctlyUsage: plotcsv.py <filename.csv> [options]

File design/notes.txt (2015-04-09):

To produce GERBER manufacturing files from KICAD (pcbnew)

1) Choose File->Plot
2) select Plot Format 'Gerber', output directory '../Gerbers/', select layers
   a. see 'digired-gerber-files-output.png'
   b. press 'PLOT'
3) in the same window, press 'Generate Drill File'
   a. see 'digired-drill-files-output.png'
   b. press 'Drill File'
   c. press 'Map File'
   d. press 'Report File'
      1. choose ../Reports/DigiRED_v1.0-drl.rpt'

To compare Gerber files

1) download and install 'gerbv'
   a. see http://gerbv.geda-project.org/
2) Load a full set of gerber files, and set the rendering color to WHITE
   a. turn all layers OFF (to prevent re-rendering while colors are changed)
   b. select each layer, press F6
   c. set the R=255, G=255, B=255
3) Load the comparison set of gerber files, and set the rending color to WHITE
   a. see 2) above
   b. alternatively, you can edit the project file and set each layer color to #(65535 65535 65535)
4) Fit all layers into the rendering window
   a. Select Layer->All On
   b. View->Rendering->Fast
   c. View->Best Fit
5) Prepare to compare
   a. Select Layer->All Off
   b. View->Rendering->Fast(XOR)
6) select pairs of matching layers to enable.  Each pair you enable will be rendered in XOR and differences highlighted.  if there are no differences, the resulting image will be black.

To translate Gerber files to PDF:

1) download 'gerber2pdf.py'
   a. see http://pages.swcp.com/~jchavez/gerber2pdf.html
2) ensure dependencies are satisfied
   a. dos> pip install plex
   b. dos> pip install reportlab
3) python gerber2pdf.py
   a. follow the prompts.  Choose 'fit to page=1' to get any output
   b. gerber.pdf is produced in the same folder as the first gerber file in the list

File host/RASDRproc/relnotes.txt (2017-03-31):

RASDRproc v0.2.5.4 -  Jan 22, 2017
==================================

RASDRproc.exe is the open-source version of the RASDR device setup and data collection program
RASDRproc_d.exe is a debug version that opens a DOS console which writes diagnostic data out

The program is able to configure RASDR2 and RASDR3 devices, set sample rates and receiver parameters.  It can optionally also display received data in time and frequency domain, I vs Q and total power.  Data collected may be saved to ASCII output files for further analysis and post-processing.

System Requirements:

1. Windows (XP or later) machine.  Dual core machines will work but a quad (or larger) core system is recommended.
2. Lime Microsystems/Myriad RF - DigiRed board with Myriad RF board ("RASDR2").
3. USB 2 or USB 3 port.
4. SARA "RASDR Radio Astronomy SDR Rx Interface" driver.

Usage:

Connect a RASDR2 device to the USB port of your computer (see the RASDR user manual for details on assigning the driver).  Double-click either RASDRproc or RASDRproc_d and wait for it to configure the device.  If you see non-zero values for "chip: rev: mask:" in the lower-left corner of the screen, it has connected to the RASDR device successfully.  Otherwise, you may still use the GUI functions to setup the configuration file.

At this point, you may press 'Start Acquisition' and observe the data collection.

When you close the program, the last set of parameters used will be written to the "RASDR.cfg" file for use next time.  RASDRproc produces annotated configuration files whose settings are described in the file itself.  It is compatible with the (un-annotated) ASCII configuration files used by RASDRviewer 1.2.2.2 and BELOW.

DC Offset Correction:

RASDRproc employs *post* acquisition DC Offset Correction.  The calibration procedure is as follows:

1) Setup the desired acquisition parameters and start data collection.  While collecting data, connect a 50ohm load to the RX of the receiver.  With v0.2.3.7+, you may also select the RX input to 'disconnect'.  While this is not a 50ohm load (rather a High-Z) it can still be useful for adjusting the DC offset. 

2) From the 'Performance Parameters' menu, select 'Tuning Parameters'.  This brings up a pop-up window where an I and Q offset is able to be entered.  While data is being collected, press the 'Use Current Averages' and observe that the values are updated. Then, press 'OK Accept Values' and see that the DC offset correction is applied.

The calibration values are saved along with the other parameters in the RASDR.cfg file.

If necessary, repeat the above procedure to compute new offsets.  Typically, it has not been seen that the offset needs to be corrected continuously, but the offset IS different each time the RASDR2 device is powered up and it does depend on what antenna system and front end electronics are connected to the RASDR RX port, as well as the sampling rate and gain settings.

NEW with v0.2.3.4:  The DC calibration can be made from the front panel.  A measure of the difference between ideal is calculated and displayed continuously according to the Mean-Square-Error formula:

MSE = ((DCOffsetI - avgI)^2 + (DCOffsetQ - avgQ)^2) / 2.0

CHANGED with v0.2.3.8:  Added a measure of the %-difference from the maximum ADC value that the DC offset is set to.  The background color of the skew metric is now as follows:

If the PERCENT is < 5.0 the display will be gray
If the PERCENT is 5.0 < 10.0, the display will be yellow
If the PERCENT is > 10.0, the display will be red

The option to do automatic (continuous) DC offset calibration (that was the only option in RASDRviewer 1.2.2.2 and BELOW) is restored with a check-box in RASDRproc v0.2.3.4 and above.

NOTE: there is a DC offset adjustment that is performed on the LMS chip as part of tuning, but currently it is an open-loop procedure that is does not produce optimal result.  Future revisions may address this issue.

Auto Restart:

RASDR2 devices when used in USB3 on marginal machines exhibit a stall acquiring data.  It has been shown that if data acquisition is stopped, then started dataflow may recover (but not always).  In those cases, the driver must be closed and re-opened, and then dataflow recovers.  This version of RASDRproc implements a detection and mitigation for this condition.  It is enabled by checking the 'Auto Restart' tick box in the upper right corner near the frame rate display.

In addition, this version annotates the data rate and frame rate display with a comparision to the expected rates and uses a RED or YELLOW background if the program is not keeping up.  The thresholds are fixed at compile time at the moment.

With v0.2.3.6, some aspects of this have changed.  Users have reported random application crashes and these appear to be related to thread-safety issues which are endemic in the code architecture.  A small amount of safety w/r/t the access to the endpoint data structures and the CyUSB library was put into place, and it seems to have a positive effect upon the liklihood of an application crash when stopping.  I have a low-spec development system in which USB3 operation is extremely marginal, calling for frequent resets of the USB device.

Gain, Bandwidth and LNA Selection:

With v0.2.3.7, some aspects of this have changed.  Changing gain values for the VGA and LNA as well as the LPF filter bandwidth now takes place immediately upon selection.  I.e. it is not required to 'Apply' which would cause an acquisition stop, configure and acquisition start cycle.  The only setting that requires an 'Apply' is the changing of the 'RF Ctr Freq' (and that is only due to more complex GUI issues than any actual restriction in the LMS6002D).  The 'Apply' button has been moved and renamed to be near the entry field.

Further, with v0.2.3.7, the ability to select which LNA port is active on the LMS6002D chip is available.  However, testing has shown that LNA1 is the only viable port; LNA3 does not appear to provide a useful response in tests conducted at 408MHz (even though it *should*).  Additionally, the RX->LNA switching that is available on the DigiRed board is now exposed.  This means that the user can disconnect the LMS6002D from the RX input to measure internal system behavior.  NOTE: it does not provide a 50ohm input to the LNA, rather it provides a Hi-Z.  This is the way that the circuit is wired on the DigiRed, and identifies an area of inprovement in the next design.

The bottom row status is updated to provide additional details on the specification of the input selected.

Radio Sky Spectrograph Integration:

This version supports a TCP/IP connection to allow Radio Sky Spectrograph to manage the display of a waterfall.  The protocol is described here:
http://cygnusa.blogspot.com/2015/07/how-to-talk-to-radio-sky-spectrograph.html

in RASDRproc the TCP/IP server, if enabled, will be active during periods of active acquisition (after pressing 'Start Acquisition').  In RSS, you tell it to use the 'RTL Dongle Receiver' under the Radio menu.  The connection is established by RSS when you press 'Start' on its GUI.  If you change certain parameters in RASDRproc or otherwise affect the frequency plan, the connection will disconnect and you can re-start by 'Start' on the RSS screen.  It seems to be pretty robust.  Please do make sure that RASDRproc RSS output is enabled and acquiring data *first* before pressing 'Start' on RSS.  Otherwise, it may take some time for it to timeout.

The RSS control panel (in RASDRproc Define Output->Setup RSS Output menu) has several tunable parameters:

- Channel Offset
- Channel Gain
- Channel Bias

These affect the calculation of the spectrum output as follows:  S[n] = (( s[n] + offset ) * gain ) + bias

- Minimum Value (clip)
- Maximum value (clip)

These will enforce the spectral outputs to limit values

- Frequency Offset

This can be used if you are using an upconverter to provide the correct offset frequency so that RSS will display the actual RF frequency instead of the IF frequency that the RASDR unit is tuned to.  NOTE: by rights, this is needed to be known by RASDRproc itself, but so far it was not implemented that way.  In the future this control may move to a different place, but for now it is listed here with the RSS stuff.

There was a regression in v0.2.3.4 in which the RSS control panel settings became unavailable.  This was corrected in v0.2.3.5 (and hopefully from now on). 

NEW with v0.2.5.2:  The "Extended RSS" protocol is implemented as described here:
https://github.com/myriadrf/RASDR/issues/16

In a nutshell, the RASDRproc program acts as a TCP server and listens for a connection on the port defined by the 'Setup RSS Output' as described above.  Configure your external program to connect to this IP:PORT combination.  Upon a connection, RASDRproc accepts the connection and sends an 1024-byte ASCII string as a response.  The response will be key value combinations separated by the "|" character.

The following keys will be provided:
    [CenterFrequencyHertz] The tuned center frequency in Hz
    [BandwidthHertz] The bandwidth of the observation in Hz
    [OffsetHertz] The offset frequency (in case an LNB or up/down converter is used with the receiver)
    [NumberOfChannels] The number of frequency bins that will be provided for each scan line

The following keys may be provided:
    [IntegrationTimeSec] The amount of integration in seconds that will be used for each scan line
    [GainDb] The total amount of receiver gain used
    [NotesString] An ASCII string provided by the program to describe the observation (excluding the "|" character).

For example:
    CenterFrequencyHertz 21000000|BandwidthHertz 5000000|OffsetHertz 0|NumberOfChannels 2048|

This would tell your program that the center frequency of the observation is 21 MHz. The bandwidth is 5 MHz, so the display will run from 21 + 2.5 to 21 - 2.5 MHz, or 18.5 MHz to 23.5 MHz. There is no offset so no frequency converter is used. Finally, NumberOfChannels denotes the number of channels that will be reported for each of the spectrum scans. There is no predefined limit on the number of channels, but the number is limited to a 4-byte unsigned integer. The connection block will be a fixed-size of 1024 bytes. Each of these parameters is separated by the pipe symbol "|". The parameter string will end with a CRLF. There may be trailing NUL to complete the 1024-byte connection block description.

Following this, a constant stream of binary data will be provided. It is not necessary to interpret the connection block (above) as the binary stream will self-describe itself. It will consist of the following binary data elements (equivalent to a binary-version of the rtl-power specification) ***in Network Byte Order***:
    [timestamp] IEEE-754 8-byte double representing the seconds since January 1, 1970 (the Unix Epoch)
    [hz_low] IEEE-754 4-byte float representing the center frequency of the lowest frequency bin
    [hz_high] IEEE-754 4-byte float representing the center frequency of the highest frequency bin
    [hz_step] IEEE-754 4-byte float representing the difference between two adjacent frequency bins
    [samples] A 4-byte unsigned integer representing the number of samples used to integrate each frequency bin
    [channels] A 4-byte unsigned integer representing the number of frequency bins to follow
    [db-values] IEEE-754 4-byte float * channels (as given in the header above)

At the moment, as with the Radio-Sky-Spectrograph version, any changes to the acquisition parameters will close the socket, requiring a re-connection.  Subsequent edits will eliminate this need and simply update the stream header dynamically.  If new metadata is desired, disconnect and re-connect to obtain it.

In v0.2.5.4, a bug was fixed in the "Extended RSS" protocol:  The extended RSS protocol is intended to write frequency values from low frequency to high frequency, in order to match the rtl-power format.  Prior to this, it was writing values from high to low frequency like the standard RSS protocol requires.  Also, the timestamping code was updated slightly to propagate it through the buffers.  A future release will introduce a reworked buffer and thread management code.

Background Subtraction:

RASDRproc has had the ability to perform live background subtraction on incoming spectral data.  However, this capability was not fully fleshed out until v0.2.3.8, when several adjustments were made including the exposure of the configuration settings to the Tuning Parameters dialog.

To access the controls, from the 'Performance Parameters' menu, select 'Tuning Parameters'.  This brings up a pop-up window and there are two sections that affect the background subtraction:  'Spectral Averaging' and 'Spectral Background Subtraction'.  Both of these are dynamic in that they can be applied while data collection is active.

>> Spectral Averaging

The two controls here are 'Unlimited Averaging' and 'Reference to ADC Full Scale'.  Both of these features are not yet implemented.

>> Spectral Background Subtraction

In this section there are the following controls:

- Enable

This is used to activate the subtraction of a background level present at the time that the 'SetPwrRef' button is pressed on the main panel.  For testing convenience, a button 'Set Reference' is also provided on the pop-up window to allow adjustments while viewing the response on the main panel.  If this box is checked, then the spectral plot will will display the result of this equasion:

PWR[f] = 10 * log10( (AVG(I[f]^2 + Q[f]^2) - REF[f]) * G )

Where I[f], Q[f] are the normalized FFT outputs.  G is the 'Integration Gain' which is adjustable on the panel.  REF[f] is obtained at the time the 'SetPwrRef' or 'Set Reference' buttons are pressed.  It is computed according to the method control described below.

Please note, that the code does not perform the SQRT of the I,Q data as part of the averaging.  It incorporates the SQRT by using a 10* instead of 20* for the power spectral density calculation.

Also note, the current version of RASDRproc operates as if a rectangular window is applied to the time domain data prior to computing the FFT.  I.e. no windowing function is applied and no overlap of the FFT samples are performed.  Future versions may address this issue.

- Visible

This control determines whether or not the in-use background level is displayed or not.  If ticked, the current background waveform will be overlaid on the spectral plot in green.

- Method

This drop-down box determines the algorithm used to compute the REF[f] vector.  There are four possible choices, described below:

    Mean:  This computes the mean value of the AVG(I[f]^2 + Q[f]^2) vector.  Typically, this selection tends to over estimate the background due to the contributions of the DC imbalance.  This is a scalar background, so that each element of REF[f] is set to this scalar value and so is applied equally to all the frequencies.
    Median:  This computes the median value of the AVG(I[f]^2 + Q[f]^2) vector.  Typically, this selection estimates the background level very well, but depends on a flat baseline.  It is not sensitive to the DC imbalance.  Again, this is a scalar background, so that each element of REF[f] is set to this scalar value and so is applied equally to all the frequencies.
    Histogram:  This computes a histogram of the of the 10 * log10( AVG(I[f]^2 + Q[f]^2) ) vector converted to integers.  It is operated on the logarithm scale to reduce the range of values that are used.  Following the selection, the reference level is recalculated to the linear value that matches the AVG() vector.  Typically, this selection slightly under-estimates the background level, but depends on a flat baseline.  It is not sensitive to the DC imbalance.  Again, this is a scalar background, so that each element of REF[f] is set to this scalar value and so is applied equally to all the frequencies.
    Vector:  This setting uses the AVG(I[f]^2 + Q[f]^2) vector as the background directly.

- Integration Gain

This allows an adjustment to the 'G' parameter in the equasion for computing the power spectral density.  The intent is to provide a weighting factor to the residual energy remaining after the background is removed.

Update plots:

As of v0.2.3.8, the 'Update Plots' checkbox at the top left of the UI window operates correctly.  Previously, if this was unchecked, no FFTs were performed and not output was produced.  This has been fixed; FFTs and output (particularly to RSS) continue to be produced although the spectral and time domain plots no longer update.  On marginal computer systems this increases the frame rate considerably.  It is recommended for unattended data collection.

Known Issues:

1) The program will give an ugly dialog box if it cannot find its settings file 'RASDR.cfg', but will create a new one when the program exits.

2) When using USB 3 on a marginal machine (e.g. dual core, 4GB RAM) the application is known to stop acquiring data.  With the updated Cypress WHQL driver, this condition can be cleared by manually stopping then restarting acquisition.  It is not yet understood why this occurs.  This behavior has not been observed on a more robust machine (e.g. quad core, 8GB RAM).  The working theory at this point is that RASDRviewer/RASDRproc and its use of the Cypress driver API requires two cores to itself and OS activity can interfere with the timing of completion requests for USB buffers.

One very strong driver of this condtion was the use of burst mode transfer for USB3 super speed.  When the burst length is set to 1, the effect it has on a lower spec machine is dramatic.  Unfortunately, it was not the only thing needed, and in some rare cases a glitch was still observed to occur.  For this reason, a workaround was found to allow data to keep being collected.

3) Scaling of the frequency plot, the use of markers and other aspects of the UI can produce unsatisfactory results.  Please be persistent in your efforts to make the plot look they way you want it.  RASDRproc v0.2.2.1 has for all intents and purposes solved the issues with the Power Plot.  Please let us know if you find a behavior that is unsatisfactory.

4) "RASDRproc.exe", if started w/o a RASDR device connection may take a very long time to start.  This does not seem to be the case with "RASDRproc_d.exe"

5) Sometimes when restarting (or if Auto Restart) is enabled, the program will raise an exception in the CCyUSBEndPoint::FinishDataXfer() as it deletes buffers.  This is when the stop is initiated by a call to LMLL_Testing_StopSdramRead() to stop collecting data from the USB stream.

Debugging this has identified thread safety issues due to concurrent access to the endpoint functions exposed by the CyUSB API.  An attempt at addressing these had been made in v0.2.3.6 and field testing is in progress.  With v0.2.3.8 a STOP/START no longer de-allocates buffers; buffers are only de-allocated if the FFT parameters are changed.

6) If choosing a high sample rate with a lot of integration, please be patient for the FFT spectrum window.  The first spectra will not be available until after the first integration time is complete.  You can estimate the ETA by observing the frame rate and dividing that from the 'average over frames' value.

7) When using FFT plot markers, the font is not a fixed-width font, and so when there is a '1' displayed, the string shifts around and is distracting.  Need to figure out how to create and use a fixed-width font instead.  Some references:
https://www.opengl.org/archives/resources/features/fontsurvey/#tmt
http://diyhpl.us/~bryan/irc/darpa/avm/meta/meta/QRG/code-library/lisp/opengl/_devel/glfont2/glfont.htm

8) If attempting to run RASDRproc on a machine via remote desktop, it can fail due to an OpenGL context not being available.  With v0.2.3.7, hopefully this will result in an informative message.  There should not be a reason why an OpenGL application cannot operate the same regardless of whether it is started on the console or via a remote desktop connection.  If the application is *already running*, there seems to be no problem with operating over remote desktop...

UPDATE: this issue has been characterized and is due to the use of Vertex Buffer Object in a way that is incompatible with the OpenGL system that is exposed to the application when it is launched under remote desktop.  It is interesting that once an appliation is running, a remote desktop connection can be made and it silently switches without incident; it is only at application start that the code is has an issue.  A branch to investigate and characterize this has been made and the fruits of its labor will eventually make it into the master release branch:
https://github.com/myriadrf/RASDR/compare/proj_ogl

9) LNA3 (which is now available to be used) does not seem to provide any meaningful response in the system.

10) When subtracting backround, the 'Mean' algorithm over-estimates the background.  This leads to a situation in which a negative residual remains after removal of the baseline.  This will appear as a minimum value (-370.0) on the spectral plot.  Some experimentation is required when attempting to make use of the background subtraction feature.

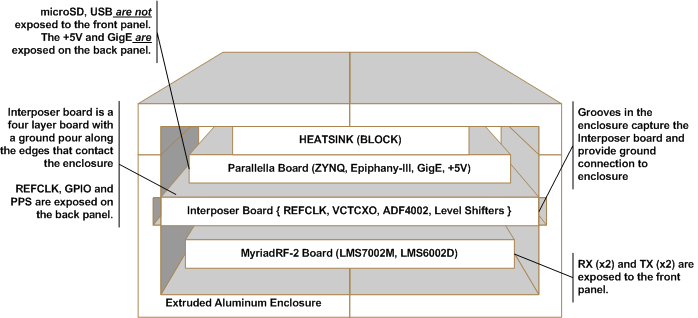
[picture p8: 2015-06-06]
design/rasdr3-concept.png

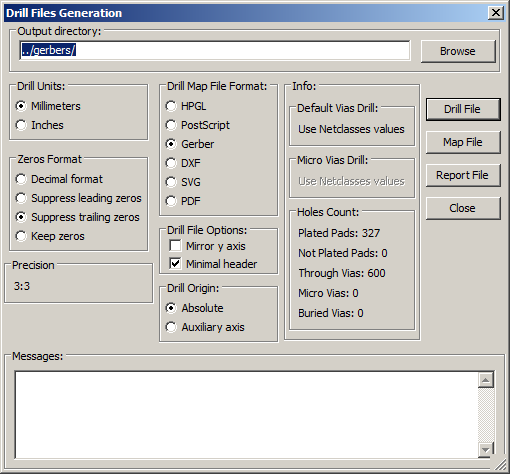
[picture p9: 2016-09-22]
design/digired-drill-files-output.png

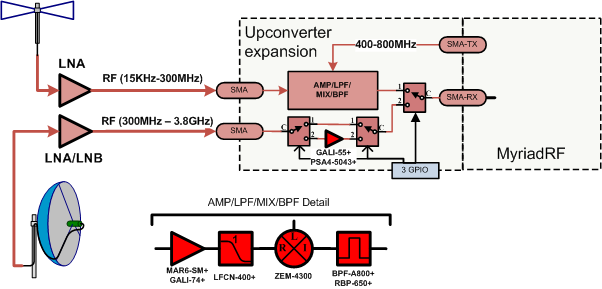
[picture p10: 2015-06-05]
design/rasdr-upconverter.png

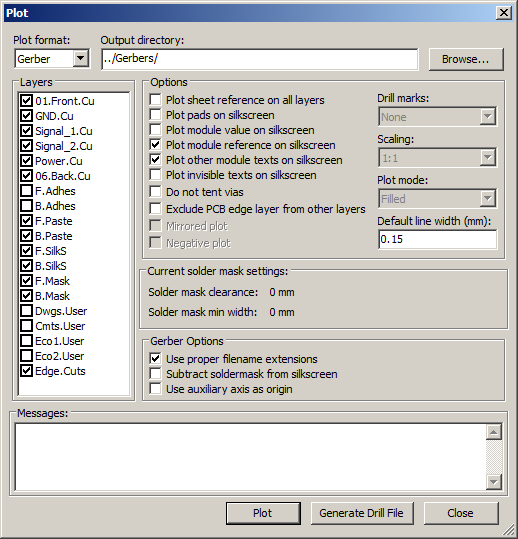
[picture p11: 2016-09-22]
design/digired-gerber-files-output.png

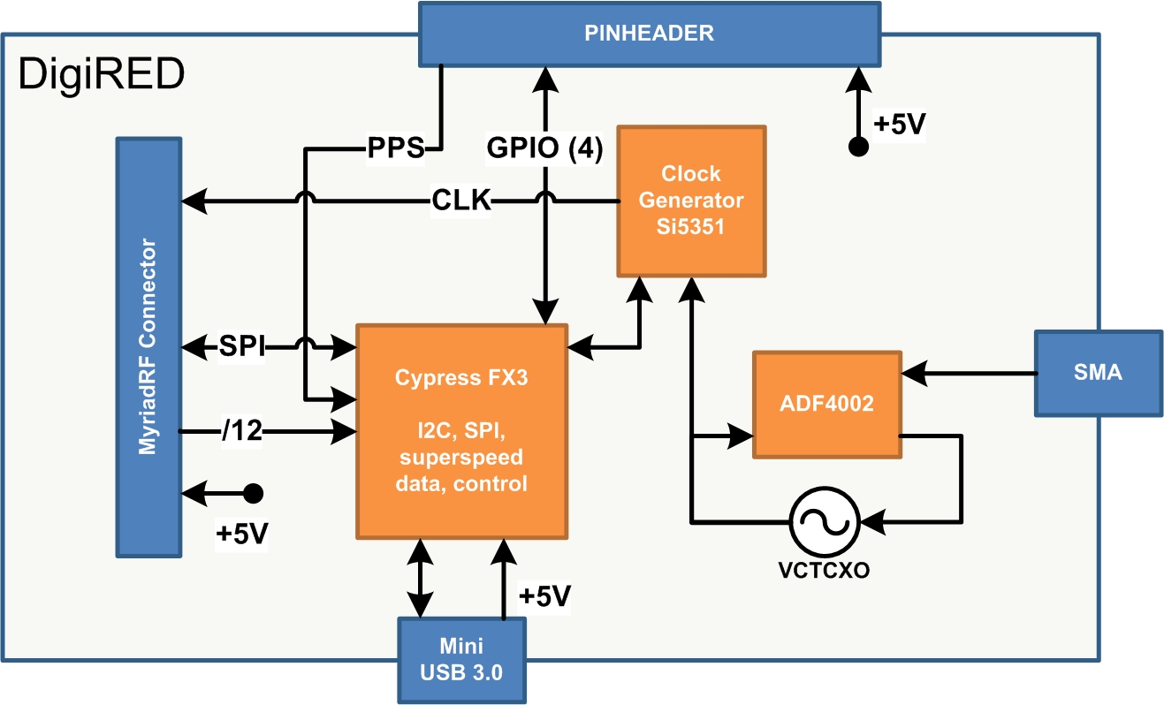
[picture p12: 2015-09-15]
design/Digired-Block-Diagram.jpg

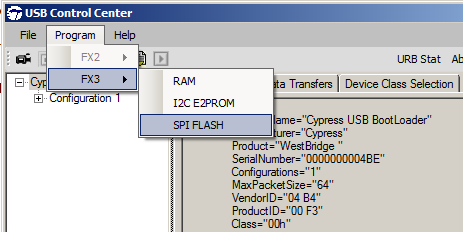
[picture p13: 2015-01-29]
host/CyControl/docs/rasdr-cycontrol-program-spi.png

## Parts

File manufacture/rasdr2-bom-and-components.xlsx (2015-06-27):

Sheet: Summary
QTY | Cost/unit | Total Cost
100 | $412.57 | $41257.00
25 | $745.29 | $18632.25
10 | $1241.01 | $12410.10

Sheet: qty=100
Date | Manufacturer | Part # | Description | Units | Unit Price | Lead Time | NRE | Setup | Parts | Assembly | Shipping | Qty | Cost/Unit | Cost/Unit (w/NRE)
2015-05-01 | Digikey | 277-5815-ND | PAN MNT HEADER 3.81MM SOLD 8POS | 100 | 7.82 | 0 |  |  | $782 |  |  | 1 | $7.82 | $7.82
2015-05-01 | Digikey | 277-5722-ND | TERM BLOCK PLUG 8POS STR 3.81MM | 100 | 7.38 | 0 |  |  | $738 |  |  | 1 | $7.38 | $7.38
2015-05-01 | Digikey | 277-6017-ND | M2 X 8 SCREW/WASHER/NUT 3PC SET | 400 | 0.17 | 0 |  |  | $66.24 |  |  | 4 | $0.66 | $0.66
2015-05-01 | Digikey | CWI495-ND | SWITCH SLIDE SPDT 500MA 125V | 100 | 1.03 | 0 |  |  | $103.35 |  |  | 1 | $1.03 | $1.03
2015-05-01 | Digikey | 29316K-ND | MACHINE SCREW PAN SLOTTED M3 | 400 | 0.24 | 0 |  |  | $95.92 |  |  | 4 | $0.96 | $0.96
2015-05-01 | Digikey | H772-ND | WASHER SPLIT LOCK M3 STEEL | 400 | 0.04 | 0 |  |  | $17.04 |  |  | 4 | $0.17 | $0.17
2015-05-01 | Digikey | 3119K-ND | WASHER FLAT #6 FIBRE | 400 | 0.03 | 0 |  |  | $11.2 |  |  | 4 | $0.11 | $0.11
 | Digikey | 24390K-ND | HEX STANDOFF M3 BRASS 5MM | 400 | 0.43 | 0 |  |  | $171.72 |  |  | 4 | $1.72 | $1.72
2015-05-01 | Digikey | WM2569-ND | CONN TERM FEMALE 22-24AWG TIN | 800 | 0.11 | 0 |  |  | $86.944 |  |  | 8 | $0.87 | $0.87
2015-05-01 | Digikey | WM2800-ND | CONN HOUSING 2POS .100 SINGLE | 400 | 0.20 | 0 |  |  | $79.12 |  |  | 4 | $0.79 | $0.79
2015-05-01 | Digikey | 6712 BK005-ND | HOOK-UP STRND 24AWG BLACK 100' | 100 |  | 0 |  |  | $39.58 |  |  |  | $0.40 | $0.40
2015-05-01 | Digikey | 6712 RD005-ND | HOOK-UP STRND 24AWG RED 100' | 100 |  | 0 |  |  | $39.58 |  |  |  | $0.40 | $0.40
2015-05-01 | Digikey | 6712 WH005-ND | HOOK-UP STRND 24AWG WHITE 100' | 100 |  | 0 |  |  | $39.58 |  |  |  | $0.40 | $0.40
2015-04-01 | USBFirewire | RR-MSBFPM-06GR | USB 3.0 Extension - B to Micro-B | 100 | 10.00 | 56 |  |  | $1000 |  |  | 1 | $10.00 | $10.00
 | USBFirewire | RR-ASBS-40GR | USB 3.0 Cable - Non-Angled - Superspeed | 100 | 11.79 |  |  |  | $1179.21147 |  |  | 1 | $11.79 | $11.79
2015-04-29 | Protocase | 37981-9 | RASDR2 Rev1 (no graphics) | 100 | 55.47 | 6 | 70 |  | $5547 |  |  | 1 | $55.47 | $56.17
 | AdvancedAssembly | B52137-A | DigiRed_V1r1_2015-03-10 | 100 |  | 40 | 415 |  |  | $16250.81 |  | 1 | $162.51 | $166.66
 | AdvancedAssembly | B46798-H | MyriadRF_v1r3e1_2015-03-31 | 100 |  | 40 | 415 |  |  | $14110.16 |  | 1 | $141.10 | $145.25
 |  |  |  | 100 |  |  |  |  |  |  | Total |  |  | $412.57

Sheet: qty=25
Date | Manufacturer | Part # | Description | Units | Unit Price | Lead Time | NRE | Setup | Parts | Assembly | Shipping | Qty | Cost/Unit | Cost/Unit (w/NRE)
2015-05-01 | Digikey | 277-5815-ND | PAN MNT HEADER 3.81MM SOLD 8POS | 25 | 9.09 | 0 |  |  | $227.275 |  |  | 1 | $9.09 | $9.09
2015-05-01 | Digikey | 277-5722-ND | TERM BLOCK PLUG 8POS STR 3.81MM | 25 | 8.58 | 0 |  |  | $214.45 |  |  | 1 | $8.58 | $8.58
2015-05-01 | Digikey | 277-6017-ND | M2 X 8 SCREW/WASHER/NUT 3PC SET | 100 | 0.24 | 0 |  |  | $24 |  |  | 4 | $0.96 | $0.96
2015-05-01 | Digikey | CWI495-ND | SWITCH SLIDE SPDT 500MA 125V | 25 | 1.22 | 0 |  |  | $30.48 |  |  | 1 | $1.22 | $1.22
2015-05-01 | Digikey | 29316K-ND | MACHINE SCREW PAN SLOTTED M3 | 100 | 0.28 | 0 |  |  | $27.8 |  |  | 4 | $1.11 | $1.11
2015-05-01 | Digikey | H772-ND | WASHER SPLIT LOCK M3 STEEL | 100 | 0.04 | 0 |  |  | $4.26 |  |  | 4 | $0.17 | $0.17
2015-05-01 | Digikey | 3119K-ND | WASHER FLAT #6 FIBRE | 100 | 0.03 | 0 |  |  | $3.25 |  |  | 4 | $0.13 | $0.13
 | Digikey | 24390K-ND | HEX STANDOFF M3 BRASS 5MM | 100 | 0.43 | 0 |  |  | $42.93 |  |  | 4 | $1.72 | $1.72
2015-05-01 | Digikey | WM2569-ND | CONN TERM FEMALE 22-24AWG TIN | 200 | 0.13 | 0 |  |  | $25.68 |  |  | 8 | $1.03 | $1.03
2015-05-01 | Digikey | WM2800-ND | CONN HOUSING 2POS .100 SINGLE | 100 | 0.22 | 0 |  |  | $22.03 |  |  | 4 | $0.88 | $0.88
2015-05-01 | Digikey | 6712 BK005-ND | HOOK-UP STRND 24AWG BLACK 100' | 25 |  | 0 |  |  | $39.58 |  |  |  | $1.58 | $1.58
2015-05-01 | Digikey | 6712 RD005-ND | HOOK-UP STRND 24AWG RED 100' | 25 |  | 0 |  |  | $39.58 |  |  |  | $1.58 | $1.58
2015-05-01 | Digikey | 6712 WH005-ND | HOOK-UP STRND 24AWG WHITE 100' | 25 |  | 0 |  |  | $39.58 |  |  |  | $1.58 | $1.58
2015-04-01 | USBFirewire | RR-MSBFPM-06GR | USB 3.0 Extension - B to Micro-B | 25 | 12.50 | 56 |  |  | $312.5 |  |  | 1 | $12.50 | $12.50
 | USBFirewire | RR-ASBS-40GR | USB 3.0 Cable - Non-Angled - Superspeed | 25 | 14.45 |  |  |  | $361.25 |  |  | 1 | $14.45 | $14.45
2015-04-29 | Protocase | 37981-9 | RASDR2 Rev1 (no graphics) | 25 | 75.00 | 6 | 70 |  | $1875 |  |  | 1 | $75.00 | $77.80
 | AdvancedAssembly | B52137-A | DigiRed_V1r1_2015-03-10 | 25 |  | 40 | 415 |  |  | $8284.51 |  | 1 | $331.38 | $347.98
 | AdvancedAssembly | B46798-H | MyriadRF_v1r3e1_2015-03-31 | 25 |  | 40 | 415 |  |  | $6158.17 |  | 1 | $246.33 | $262.93
 |  |  |  | 25 |  |  |  |  |  |  | Total |  |  | $745.29

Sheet: qty=10
Date | Manufacturer | Part # | Description | Units | Unit Price | Lead Time | NRE | Setup | Parts | Assembly | Shipping | Qty | Cost/Unit | Cost/Unit (w/NRE)
2015-05-01 | Digikey | 277-5815-ND | PAN MNT HEADER 3.81MM SOLD 8POS | 10 | 9.09 | 0 |  |  | $90.91 |  |  | 1 | $9.09 | $9.09
2015-05-01 | Digikey | 277-5722-ND | TERM BLOCK PLUG 8POS STR 3.81MM | 10 | 8.58 | 0 |  |  | $85.78 |  |  | 1 | $8.58 | $8.58
2015-05-01 | Digikey | 277-6017-ND | M2 X 8 SCREW/WASHER/NUT 3PC SET | 40 | 0.26 | 0 |  |  | $10.272 |  |  | 4 | $1.03 | $1.03
2015-05-01 | Digikey | CWI495-ND | SWITCH SLIDE SPDT 500MA 125V | 10 | 1.25 | 0 |  |  | $12.46 |  |  | 1 | $1.25 | $1.25
2015-05-01 | Digikey | 29316K-ND | MACHINE SCREW PAN SLOTTED M3 | 40 | 0.38 | 0 |  |  | $15.28 |  |  | 4 | $1.53 | $1.53
2015-05-01 | Digikey | H772-ND | WASHER SPLIT LOCK M3 STEEL | 40 | 0.04 | 0 |  |  | $1.704 |  |  | 4 | $0.17 | $0.17
2015-05-01 | Digikey | 3119K-ND | WASHER FLAT #6 FIBRE | 40 | 0.05 | 0 |  |  | $2.12 |  |  | 4 | $0.21 | $0.21
 | Digikey | 24390K-ND | HEX STANDOFF M3 BRASS 5MM | 40 | 0.56 | 0 |  |  | $22.4 |  |  | 4 | $2.24 | $2.24
2015-05-01 | Digikey | WM2569-ND | CONN TERM FEMALE 22-24AWG TIN | 80 | 0.14 | 0 |  |  | $11.072 |  |  | 8 | $1.11 | $1.11
2015-05-01 | Digikey | WM2800-ND | CONN HOUSING 2POS .100 SINGLE | 40 | 0.32 | 0 |  |  | $12.6 |  |  | 4 | $1.26 | $1.26
2015-05-01 | Digikey | 6712 BK005-ND | HOOK-UP STRND 24AWG BLACK 100' | 10 |  | 0 |  |  | $39.58 |  |  |  | $3.96 | $3.96
2015-05-01 | Digikey | 6712 RD005-ND | HOOK-UP STRND 24AWG RED 100' | 10 |  | 0 |  |  | $39.58 |  |  |  | $3.96 | $3.96
2015-05-01 | Digikey | 6712 WH005-ND | HOOK-UP STRND 24AWG WHITE 100' | 10 |  | 0 |  |  | $39.58 |  |  |  | $3.96 | $3.96
2015-04-01 | USBFirewire | RR-MSBFPM-06GR | USB 3.0 Extension - B to Micro-B | 10 | 14.50 | 56 |  |  | $145 |  |  | 1 | $14.50 | $14.50
 | USBFirewire | RR-ASBS-40GR | USB 3.0 Cable - Non-Angled - Superspeed | 10 | 16.45 |  |  |  | $164.5 |  |  | 1 | $16.45 | $16.45
2015-04-29 | Protocase | 37981-9 | RASDR2 Rev1 (no graphics) | 10 | 105.78 | 6 | 70 |  | $1057.8 |  |  | 1 | $105.78 | $112.78
 | AdvancedAssembly | B52137-A | DigiRed_V1r1_2015-03-10 | 10 |  | 40 | 415 |  |  | $6119.34 |  | 1 | $611.93 | $653.43
 | AdvancedAssembly | B46798-H | MyriadRF_v1r3e1_2015-03-31 | 10 |  | 40 | 415 |  |  | $3640.1 |  | 1 | $364.01 | $405.51
 |  |  |  | 10 |  |  |  |  |  |  | Total |  |  | $1241.01

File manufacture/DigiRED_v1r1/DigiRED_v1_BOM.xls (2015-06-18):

No | Value | Qty | Designator | Package | Description | Manufacturer Part Number | Manufacturer | Vendor | Vendor Part Number | Assemble | Alternate
1 | 13pF | 2 | C9 C10 | C_SM0402 | CAP, CER, 13PF, 50V, 5%, NP0, 0402, | 500R07S130JV4T | Johanson Technology Inc | Digi-Key | 712-1259-1-ND
2 | 22pF | 3 | C5 C65 C66 | C_SM0402 | CAP, CER, 22PF, 50V, 5%, NPO, 0402, | CC0402JRNPO9BN220 | Yageo | Digi-Key | 311-1018-1-ND
3 | 220pF | 1 | C54 | C_SM0402 | CAP, CER, 220PF, 50V, 10%, X7R, 0402, | CC0402KRX7R9BB221 | Yageo | Digi-Key | 311-1035-1-ND
4 | 560pF | 1 | C29 | C_SM0402 | CAP, CER, 560PF, 50V, 10%, X7R, 0402, | CC0402KRX7R9BB561 | Yageo | Digi-Key | 311-1029-1-ND | NOFIT
5 | 10nF | 10 | C24 C30 C33 C35 C37 C40 C44 C45 C49 C51 | C_SM0201 | CAP, CER, 10000PF, 10V, 10%, X5R, 0201, | CC0201KRX5R6BB103 | Yageo | Digi-Key | 311-1409-1-ND
6 | 10nF | 2 | C6 C64 | C_SM0402 | CAP, CER, 10000PF, 25V, 10%, X7R, 0402, | CC0402KRX7R8BB103 | Yageo | Digi-Key | 311-1337-1-ND
7 | 0.1uF | 16 | C18 C19 C20 C21 C23 C25 C28 C31 C32 C38 C39 C41 C42 C43 C47 C48 | C_SM0201 | CAP, CER, 0.1UF, 6.3V, 10%, X5R, 0201, | CC0201KRX5R5BB104 | Yageo | Digi-Key | 311-1408-1-ND
8 | 0.1uF | 14 | C2 C4 C12 C14 C53 C55 C56 C57 C58 C59 C60 C61 C62 C63 | C_SM0402 | CAP, CER, 0.1UF, 16V, Y5V, 0402, | CC0402ZRY5V7BB104 | Yageo | Digi-Key | 311-1047-1-ND
9 | 1uF | 2 | C22 C27 | C_SM0402 | CAP, CER, 1UF, 6.3V, Y5V, 0402, | CC0402ZRY5V5BB105 | Yageo | Digi-Key | 311-1377-1-ND
10 | 2.2uF | 3 | C26 C36 C46 | C_SM0603 | CAP, CER, 2.2UF, 6.3V, 10%, X5R, 0603, | CC0603KRX5R5BB225 | Yageo | Digi-Key | 311-1449-1-ND
11 | 4.7uF | 2 | C17 C34 | C_TANT_SM0603 | CAP, TANT, 4.7UF, 16V, 20%, 0603, | TR8M475M016C4000 | Vishay Sprague | Digi-Key | 718-1676-1-ND
12 | 10uF | 2 | C50 C52 | C_SM0603 | CAP, CER, 10UF, 6.3V, 20%, X5R, 0603, | CC0603MRX5R5BB106 | Yageo | Digi-Key | 311-1448-1-ND
13 | Green | 3 | D1 D2 D9 | LD_0603 | LED GREEN, CLEAR, 0603 SMD, | LTST-C190KGKT | Lite-On Inc | Digi-Key | 160-1435-1-ND
14 | Yellow | 3 | D6 D7 D8 | LD_0603 | LED, YELLOW, RECT CLEAR, 0603, | LTST-C194KSKT | Lite-On Inc | Digi-Key | 160-1836-1-ND
15 | CONN_2X1 | 1 | J2 | TH_PINHD-1X2_RA | SIL, HORIZ PC TAIL, PIN HEADER, | M20-9960245 | Harwin Inc | Digi-Key | 952-2244-ND
16 | 19.2MHz | 1 | Q2 | SM_XO | CRYSTAL 19.200000MHZ, 13PF, SMD, | 405C35B19M20000 | CTS-Frequency Controls | Digi-Key | CTX648CT-ND
17 | MMBT3904 | 1 | Q3 | SOT23 | TRANS, NPN, 40V, 200MA, SOT23, | MMBT3904,215 | NXP Semiconductors | Digi-Key | 568-4510-1-ND
18 | 0 | 16 | R5 R9 R48 R92 R97 R101 R102 R103 R104 R105 R117 R119 R121 R123 R125 R127 | R_SM0402 | RES, 0.0 OHM,1/16W, JUMP, 0402 SMD, | RC0402JR-070RL | Yageo | Digi-Key | 311-0.0JRCT-ND
19 | 0 | 13 | R8 R13 R16 R31 R59 R60 R100 R116 R118 R120 R122 R124 R126 | R_SM0402 | RES, 0.0 OHM,1/16W, JUMP, 0402 SMD, | RC0402JR-070RL | Yageo | Digi-Key | 311-0.0JRCT-ND | NOFIT
20 | 0 | 1 | R10 | R_SM0402 | FERRITE, CHIP BEAD, 600 OHM, SMD, | MMZ1005S601C | TDK Corporation | Digi-Key | 445-2162-1-ND
21 | 0 | 2 | R3 R132 | R_SM0805 | RES, 0.0 OHM, .33W, JUMP, 0805, SMD, | CRCW08050000Z0EAHP | Vishay Dale | Digi-Key | 541-0.0TBCT-ND
22 | 0 | 3 | R4 R133 R135 | R_SM0805 | RES, 0.0 OHM, .33W, JUMP, 0805, SMD, | CRCW08050000Z0EAHP | Vishay Dale | Digi-Key | 541-0.0TBCT-ND | NOFIT
23 | 10 | 1 | R79 | R_SM0402 | RES, 10 OHM, 1/16W, 5%, 0402, SMD, | RC0402JR-0710RL | Yageo | Digi-Key | RC0402JR-0710RL
24 | 22 | 22 | R6 R7 R33 R34 R35 R36 R37 R38 R39 R40 R41 R42 R43 R44 R45 R46 R47 R107 R109 R111 R113 R115 | R_SM0402 | RES, 22.0 OHM, 1/16W, 1%, 0402, SMD, | RC0402FR-0722RL | Yageo | Digi-Key | 311-22.0LRTR-ND
25 | 22 | 5 | R106 R108 R110 R112 R114 | R_SM0402 | RES, 22.0 OHM, 1/16W, 1%, 0402, SMD, | RC0402FR-0722RL | Yageo | Digi-Key | 311-22.0LRTR-ND | NOFIT
26 | 220R/100MHz | 2 | R54 R58 | RL_SM0805 | FERRITE CHIP, 220 OHM, 0805, | BLM21PG221SN1D | Murata Electronics North America | Digi-Key | 490-1054-1-ND
27 | 330 | 1 | R131 | R_SM0402 | RES, 330 OHM, 1/16W, 5%, 0402, SMD, | RC0402JR-07330RL | Yageo | Digi-Key | 311-330JRCT-ND
28 | 430 | 1 | R81 | R_SM0402 | RES, 430 OHM, 1/16W, 1%, 0402 SMD, | CRCW0402430RFKED | Vishay Dale | Digi-Key | 541-430LCT-ND
29 | 470 | 6 | R1 R75 R76 R77 R88 R130 | R_SM0402 | RES, 470 OHM, 1/16W, .5%, 0402 SMD, | ERA-2AED471X | Panasonic Electronic Components | Digi-Key | P470DECT-ND
30 | 750 | 1 | R87 | R_SM0402 | RES, 750 OHM, 1/16W, 1%, 0402 SMD, | CRCW0402750RFKED | Vishay Dale | Digi-Key | 541-750LCT-ND
31 | 1K | 3 | R83 R86 R93 | R_SM0402 | RES, 1.00K OHM, 1/16W, 1%, 0402 SMD, | RC0402FR-071KL | Yageo | Digi-Key | 311-1.00KLRCT-ND
32 | 1.15K | 1 | R85 | R_SM0402 | RES, 1.15K OHM, 1/16W, 1%, 0402 SMD, | CRCW04021K15FKED | Vishay Dale | Digi-Key | 541-1.15KLCT-ND
33 | 1K6 | 1 | R90 | R_SM0402 | RES, 1.60K OHM, 1/16W, 1%, 0402 SMD, | CRCW04021K60FKED | Vishay Dale | Digi-Key | 541-1.60KLCT-ND
34 | 2K2 | 4 | R94 R95 R96 R99 | R_SM0402 | RES, 2.20K OHM, 1/16W, 1%, 0402 SMD, | RC0402FR-072K2L | Yageo | Digi-Key | 311-2.20KLRCT-ND
35 | 3K | 1 | R89 | R_SM0402 | RES, 3.00K OHM, 1/16W, 1%, 0402 SMD, | CRCW04023K00FKED | Vishay Dale | Digi-Key | 541-3.00KLCT-ND
36 | 3.57K | 1 | R84 | R_SM0402 | RES, 3.57K OHM, 1/16W, 1%, 0402 SMD, | CRCW04023K57FKED | Vishay Dale | Digi-Key | 541-3.57KLCT-ND
37 | 4.7K | 3 | R63 R64 R137 | R_SM0402 | RES, 4.7K OHM, 1/16W, 1%, 0402 SMD, | RC0402FR-074K7L | Yageo | Digi-Key | 311-4.7KLRCT-ND
38 | 6.04K/1% | 1 | R70 | R_SM0402 | RES, 6.04K OHM, 1/16W, 1%, 0402 SMD, | CRCW04026K04FKED | Vishay Dale | Digi-Key | e
39 | 10K | 9 | R2 R14 R15 R72 R73 R74 R80 R91 R134 | R_SM0402 | RES, 10K OHM, 1/16W, 5%, 0402, SMD, | RC0402JR-0710KL | Yageo | Digi-Key | 311-10KJRCT-ND
40 | 30.1K | 1 | R82 | R_SM0402 | RES, 30.1K OHM, 1/16W, 1%, 0402 SMD, | CRCW040230K1FKED | Vishay Dale | Digi-Key | 541-30.1KLCT-ND
41 | 100K | 3 | R50 R52 R56 | R_SM0402 | RES, 100K OHM, 1/16W, 5%, 0402, SMD, | RC0402JR-07100KL | Yageo | Digi-Key | 311-100KJRCT-ND
42 | 200/1% | 1 | R71 | R_SM0402 | RES, 200 OHM, 1/16W, 1%, 0402 SMD, | RC0402FR-07200RL | Yageo | Digi-Key | 311-200LRCT-ND
43 | P_SWITCH | 1 | SW3 | TH_PINHD-3X1 | BERGSTIK II .100" SR STRAIGHT | 68001-403HLF | FCI | Digi-Key | 609-3471-ND
44 | T_SWITCH | 1 | SW2 | SW_B3U-1000P | SWITCH, TACTILE, SPST-NO, 0.05A, 12V, | B3U-1000P | Omron Electronics Inc-EMC Div | Digi-Key | SW1020CT-ND
45 | RACON_TXCO | 1 | TCXO1 | SMD_TXCO | 30.72 MHz, TCXO with Voltage Control Option | VFTX302-HDEBC-30.72 (http://www.ctsvalpey.com/Collateral/Documents/English-US/Products/FrequencyControl/Oscillators/TCXO/VFTX302.pdf) | CTS/Valpey | Dove | VFTX302-HDEBC-30.72 |  | E5280LF
46 | RACON_TXCO_PLUTO+ | 1 | TCXO2 | SMD_TXCO_Pluto+ | 30.72MHz, RPT7050A, Pluto+, | RPT7050A | RAKON | Rakon | E6245LF | NOFIT
47 | TP | 5 | TP1 TP2 TP3 TP4 TP5 | TP | - | - | - | - | - | NOFIT
48 | ADF4002 | 1 | U16 | 20Lead_LFCSP_VQ | IC PLL, FREQUENCY SYNTH, 20-LFCSP, | ADF4002BCPZ | Analog Devices Inc | Digi-Key | ADF4002BCPZ-ND
49 | CYUSB3011 | 1 | U2 | CYUSB3011-121-ballBGA | ARM9, USB3, CONTROLLER, X16, GPIF II, | CYUSB3011-BZXC | Cypress Semiconductor Corp | Digi-Key | 428-3179-ND
50 | SI5356 | 1 | U12 | QFN24 | IC CLK GENERATOR, 200MHZ, 24-QFN, | Si5356A-B-GM | Silicon Laboratories Inc | Mouser | 634-SI5356A-B-GM
51 | M25P40 | 1 | U6 | SOIC-8 | IC FLASH, 4MBIT, 75MHZ, 8SO, | M25P40-VMN6TPB | Micron Technology Inc | Digi-Key | M25P40-VMN6TPBCT-ND
52 | TPS76801QD | 1 | U9 | SOIC-8 | IC REG, LDO, ADJ, 1A, 8SOIC, | TPS76801QD | Texas Instruments | Digi-Key | 296-2743-5-ND
53 | TPS74801SON | 1 | U8 | SON-10 | IC REG, LDO, ADJ, 1.5A, 10SON, | TPS74801DRCR | Texas Instruments | Digi-Key | 296-21563-1-ND
54 | SN74LVC1G04DBVR | 3 | U13 U14 U15 | SOT23-5 | IC SINGLE, INVERTER-GATE, SOT-23-5, | SN74LVC1G04DBVR | Texas Instruments | Digi-Key | 296-11599-1-ND
55 | CDCV304PW | 1 | U11 | TSSOP-8 | IC CLK BUFFER 1:4, 200MHZ, 8TSSOP, | CDCV304PWR | Texas Instruments | Digi-Key | 296-9436-1-ND
56 | SP3010-04UTG | 1 | U5 | uDFN-10 | TVS ARRAY, ESD, 4CH, .45PF, 8KV, UDFN, | SP3010-04UTG | Littelfuse Inc | Digi-Key | F3507TR-ND
57 | SMA | 1 | X7 | SMA | SMA End Launch Bulkhead Jack | 132289 | Amphenol Connex | Digi-Key | ACX1426-ND |  | 142-0701-871
58 | FX10B-80S/8-SV | 1 | X1 | SMD_FX10B-80S/8-SV | CONN, RECEPT, 80POS, W/POST, SMD, | FX10A-80S/8-SV(71) | HIROSE | DigiKey | H11232-ND
59 | MINI-USB3110-30-A | 1 | X5 | SMD_USB3110 | USB3110-30-A - MICRO USB 3.0 B CONNECTOR, 10POS, SMT RT ANGLE, | USB3110-30-A | GLOBAL CONNECTOR TECHNOLOGY | Farnell | 2065838
60 | CONN_2X10 | 1 | X3 | TH_PINHD-10X2_HRA | CONN HEADER, 20POS, .100 R/A, 30AU, | 68021-120HLF | FCI | Digi-Key | 609-3338-ND
61 | CONN_2X4 | 1 | X2 | TH_PINHD-4X2_V | CONN HEADER, 8POS, .100 STR TIN, | 67997-408HLF | FCI | Digi-Key | 609-3397-ND
62 | CYUSB3011 | 1 | U1 | CYUSB3011-121-ballBGA | ARM9, USB3, CONTROLLER, X16, GPIF II, | CYUSB3011-BZXC | Cypress Semiconductor Corp | Digi-Key | 428-3179-ND | NOFIT
63 | T_SWITCH | 1 | SW1 | SW_B3U-1000P | SWITCH, TACTILE, SPST-NO, 0.05A, 12V, | B3U-1000P | Omron Electronics Inc-EMC Div | Digi-Key | SW1020CT-ND | NOFIT
64 | 4.7K | 3 | R61 R62 R136 | R_SM0402 | RES, 4.7K OHM, 1/16W, 1%, 0402 SMD, | RC0402FR-074K7L | Yageo | Digi-Key | 311-4.7KLRCT-ND | NOFIT
64 | 10K | 5 | R11 R12 R65 R66 R67 | R_SM0402 | RES, 10K OHM, 1/16W, 5%, 0402, SMD, | RC0402JR-0710KL | Yageo | Digi-Key | 311-10KJRCT-ND | NOFIT
65 | 100K | 3 | R49 R51 R55 | R_SM0402 | RES, 100K OHM, 1/16W, 5%, 0402, SMD, | RC0402JR-07100KL | Yageo | Digi-Key | 311-100KJRCT-ND | NOFIT
65 | 0 | 2 | R30 R32 | R_SM0402 | RES, 0.0 OHM,1/16W, JUMP, 0402 SMD, | RC0402JR-070RL | Yageo | Digi-Key | 311-0.0JRCT-ND | NOFIT
66 | 22 | 13 | R17 R18 R19 R20 R21 R22 R23 R24 R25 R26 R27 R28 R29 | R_SM0402 | RES, 22.0 OHM, 1/16W, 1%, 0402, SMD, | RC0402FR-0722RL | Yageo | Digi-Key | 311-22.0LRTR-ND | NOFIT
67 | 6.04K/1% | 1 | R68 | R_SM0402 | RES, 6.04K OHM, 1/16W, 1%, 0402 SMD, | CRCW04026K04FKED | Vishay Dale | Digi-Key | 541-6.04KLCT-ND | NOFIT
68 | 200/1% | 1 | R69 | R_SM0402 | RES, 200 OHM, 1/16W, 1%, 0402 SMD, | RC0402FR-07200RL | Yageo | Digi-Key | 311-200LRCT-ND | NOFIT
69 | 470 | 3 | R78 R128 R129 | R_SM0402 | RES, 470 OHM, 1/16W, .5%, 0402 SMD, | ERA-2AED471X | Panasonic Electronic Components | Digi-Key | P470DECT-ND | NOFIT
70 | Yellow | 3 | D3 D4 D5 | LD_0603 | LED, YELLOW, RECT CLEAR, 0603, | LTST-C194KSKT | Lite-On Inc | Digi-Key | 160-1836-1-ND | NOFIT
71 | 13pF | 2 | C7 C8 | C_SM0402 | CAP, CER, 13PF, 50V, 5%, NP0, 0402, | 500R07S130JV4T | Johanson Technology Inc | Digi-Key | 712-1259-1-ND | NOFIT
72 | 0.1uF | 4 | C1 C3 C11 C13 | C_SM0402 | CAP, CER, 0.1UF, 16V, Y5V, 0402, | CC0402ZRY5V7BB104 | Yageo | Digi-Key | 311-1047-1-ND | NOFIT
73 | 19.2MHz | 1 | Q1 | SM_XO | CRYSTAL 19.200000MHZ, 13PF, SMD, | 405C35B19M20000 | CTS-Frequency Controls | Digi-Key | CTX648CT-ND | NOFIT
74 | SP3010-04UTG | 1 | U3 | uDFN-10 | TVS ARRAY, ESD, 4CH, .45PF, 8KV, UDFN, | SP3010-04UTG | Littelfuse Inc | Digi-Key | F3507TR-ND | NOFIT
75 | CONN_2X1 | 1 | J1 | TH_PINHD-1X2_RA | SIL, HORIZ PC TAIL, PIN HEADER, | M20-9960245 | Harwin Inc | Digi-Key | 952-2244-ND | NOFIT
76 | M25P40 | 1 | U4 | SOIC-8 | IC FLASH, 4MBIT, 75MHZ, 8SO, | M25P40-VMN6TPB | Micron Technology Inc | Digi-Key | M25P40-VMN6TPBCT-ND | NOFIT
77 | 220R/100MHz | 2 | R53 R57 | RL_SM0805 | FERRITE CHIP, 220 OHM, 0805, | BLM21PG221SN1D | Murata Electronics North America | Digi-Key | 490-1054-1-ND | NOFIT
78 | MINI-USB3110-30-A | 1 | X4 | SMD_USB3110 | USB3110-30-A - MICRO USB 3.0 B CONNECTOR, 10POS, SMT RT ANGLE, | USB3110-30-A | GLOBAL CONNECTOR TECHNOLOGY | Farnell | 2065838 | NOFIT

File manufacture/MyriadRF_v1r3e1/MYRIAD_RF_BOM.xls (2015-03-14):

VALUE | QTY | Reference | Footprint | Description | Manufacturer Part Number | Manufacturer | Vendor | Vendor Part Number | Assemble | Alternate
0.5pF | 2 | C33 C120 | C_SM0402 | CAP; CER; 0.5PF; 50V; NPO; 0402; | CC0402CRNPO9BNR50 | Yageo | Digi-Key | 311-1001-2-ND |  | C0402C508C5GACTU
1.0pF | 3 | C21 C34 C72 | C_SM0402 | CAPACITOR; NP0; 0402; 1PF; | GJM1555C1H1R0BB01D | MURATA | Digi-Key | 490-8083-1-ND
1.2pF | 3 | C36 C44 C49 | C_SM0402 | CAP; CER; 1.2PF; 50V; NP0; 0402; | GJM1555C1H1R2BB01D | MURATA | Digi-Key | 490-8085-1-ND |  | CBR04C129B1GAC
1.8pF | 3 | C91 C92 C93 | C_SM0402 | CAP; CER; 1.8PF; 50V; NP0; 0402; | GJM1555C1H1R8BB01D | MURATA | Digi-Key | 490-8089-1-ND |  | CBR04C189B1GAC
3.9pF | 2 | C94 C95 | C_SM0402 | CAP; CER; 3.9PF; 50V; NP0; 0402; | GJM1555C1H3R9BB01D | MURATA | Digi-Key | 490-8099-1-ND |  | CBR04C399B1GAC
8.2pF | 2 | C31 C68 | C_SM0402 | CAPACITOR; NP0; 0402; 50V; 8.2PF; | C0402C829C5GACTU | KEMET | Farnell | 1865418
10pF | 1 | C221 | C_SM0402 | CAPACITOR CERAMIC 10PF 50V; C0G; 1%; 0402 | GRM1555C1H100FA01D | MURATA | Digi-Key | 490-6186-1-ND |  | 04025U100FAT2A
33pF | 13 | C53 C55 C73 C78 C105 C106 C109 C110 C111 C112 C113 C114 C115 | C_SM0402 | CAPACITOR; 0402; NP0; 33PF; 5% | GRM1555C1H330JA01D | MURATA | Digi-Key | 490-5936-1-ND |  | C0402C330J4GACTU
100pF | 13 | C26 C27 C51 C54 C56 C57 C59 C60 C61 C63 C69 C77 C101 | C_SM0402 | CAPACITOR; 0402; 100PF; 50V; | GRM1555C1H101JA01J | MURATA | Digi-Key | 490-7754-1-ND |  | CC0402JRNPO9BN101
150pF | 2 | C15 C18 | C_SM0402 | MLCC; 0402; NP0; 50V; 150PF; 5% | GRM1555C1H151JA01D | MURATA | Digi-Key | 490-3229-1-ND |  | UMK105CG151JV-F
470pF | 2 | C13 C16 | C_SM0402 | MLCC; 0402; X7R; 50V; 470PF; 10% | GRM155R71H471KA01D | MURATA | Digi-Key | 490-1300-1-ND |  | UMK105B7471KV-F
10nF | 4 | C14 C17 C25 C136 | C_SM0402 | CAPACITOR; 0402; 10NF; 16V; | CC0402KRX7R7BB103 | YAGEO (PHYCOMP) | Farnell | 3019275
100nF | 23 | C3 C4 C7...C12 C19 C35 C74...C76 C82 C84 C85 C90 C216...C220 C224 | C_SM0402 | CAPACITOR; 0402; 100NF; 10V; X5R; | C0402C104K8PACTU | KEMET | Farnell | 1288282
1uF | 5 | C1 C2 C5 C6 C20 | C_SM0402 | MLCC; 0402; X5R; 10V; 1UF; 10% | GRM155R61A102KA01D | MURATA | Digi-Key | 490-6295-1-ND |  | C1005X5R1H102K050BA
1uF | 6 | C22 C23 C81 C88 C122 C144 | C_SM0603 | CAP CER 1UF 10V 10% X5R 0603 | CC0603KRX5R6BB105 | YAGEO (PHYCOMP) | Digi-Key | 311-1443-1-ND |  | C0603C105K8PACTU
2.2uF | 2 | C24 C117 | C_SM0603 | CAPACITOR; 0603; X5R; 10V; 2.2UF; | GRM188R61A225KE34D | MURATA | Digi-Key | 490-1545-1-ND |  | C0603C225K8PACTU
10uF | 4 | C52 C83 C222 C223 | C_S0603 | CAPACITOR; 10UF; 10V; X5R; 0603; | LMK107BJ106MALTD | TAIYO YUDEN | Farnell | 2113070RL
LD1117DT33 | 1 | DA1 | DPAK2 | LD1117DT33 - V REG LDO +3.3V; SMD; 1117; DPAK-3 | LD1117DT33CTR | STMICROELECTRONICS | Digi-Key | 497-1235-1-ND
LMS6002DR2 | 1 | DA3 | DQFN-120 | LMS6002 Tranceiver; DQFN-120; | LMS6002DFN | Lime Microsystems | Digi-Key | 1434-1000-6-ND
PE42440 | 1 | DA5 | QFN-16 | IC RF SWITCH; SP4T; 50 OHM; 16QFN; | PE42440MLBB-Z | Peregrine Semiconductor | Digi-Key | 1046-1038-1-ND
PE42422 | 1 | DA6 | QFN12 | IC; RF SWITCH; SPDT; 50 OHM; 12QFN; | PE42422MLAA-Z | Peregrine Semiconductor | Digi-Key | 1046-1062-1-ND
LP2985IM5-1.8 | 2 | DA2 DA7 | SOT23-5 | LP2985IM5-1.8/NOPB - IC; REG; LDO; 1.8V; 150MA; SOT23 | LP2985IM5-1.8/NOPB | NATIONAL SEMICONDUCTOR | Farnell | 1564761RL
CDCV304PW | 1 | DA4 | TSSOP-8 | CDCV304PWR - IC; CLOCK BUFFER; | CDCV304PWR | TEXAS INSTRUMENTS | Farnell | 1703244
Shield | 1 | EK1 | EK | EMI Gaskets & Earth Pads 204 Frame | BMI-S-204-F | Laird Technologies | Mouser | 739-BMIS-204-F
4.7nH | 4 | L17 L22 L34 L35 | L_SM0402 | Inductor; 4.7 nH; 0402; 5%; | 0402HP-4N7X_LU | Coilcraft | Coilcraft | 0402HP-4N7X_LU
5.6nH | 3 | L27 L28 L29 | L_SM0402 | Inductor; 5.6 nH; 0402; 5%; | 0402HP-5N6XJLU | Coilcraft | Coilcraft | 0402HP-5N6XJLU
12nH | 3 | L32 L36 L37 | L_SM0402 | Inductor; 12 nH; 0402; 5%; | 0402HP-12NX_LU | Coilcraft | Coilcraft | 0402HP-12NX_LU
12nH | 2 | L38 L40 | L_SM0402 | Inductor; 12 nH; 0402; 5%; | 0402HP-12NX_LU | Coilcraft | Coilcraft | 0402HP-12NX_LU | NOFIT
15nH | 1 | L26 | L_SM0402 | Inductor; 15 nH; 0402; 5%; | 0402HP-15NX_LU | Coilcraft | 0402HP-15NX_LU | Coilcraft
22nH | 1 | L42 | L_SM0402 | Inductor; 22 nH; 0402; 5%; | 0402HP-22NX_LU | Coilcraft | Coilcraft | 0402HP-22NX_LU
36nH | 4 | L11 L12 L13 L33 | L_SM0402 | Inductor; 36 nH; 0402; 5%; | 0402CS-36NX_LU | Coilcraft | Coilcraft | 0402CS-36NX_LU
LED | 1 | LD1 | LD0603 | LED CHIPLED 570NM GREEN 0603 SMD | LG Q971-KN-1 | OSRAM | Digi-Key | 475-1409-1-ND
0 | 13 | R4 R12 R18 R23 R24 R25 R28 R42 R44 R46 R92 R139 R164 | R_SM0402 | RESISTOR; 0402; 0R; REEL 10000; | RC0402JR-070RL | YAGEO (PHYCOMP) | Farnell | 1117280
0 | 5 | R26 R27 R29 R49 R153 | R_SM0402 | RESISTOR; 0402; 0R; REEL 10000; | RC0402JR-070RL | YAGEO (PHYCOMP) | Farnell | 1117280 | NOFIT
0 | 2 | R1 R82 | R_SM0805 | RESISTOR; RC11; 0805; 0R; | RC0805JR-070RL | YAGEO (PHYCOMP) | Farnell | 9233750
0 | 1 | R5 | R_SM0805 | RESISTOR; RC11; 0805; 0R; | RC0805JR-070RL | YAGEO (PHYCOMP) | Farnell | 9233750 | NOFIT
22 | 7 | R16 R17 R38 R39 R45 R47 R48 | R_array | RESISTOR ARRAY; ARV341; 0804; 22R; | YC124-JR-0722RL | YAGEO (PHYCOMP) | Farnell | 9235264
22 | 2 | R74 R75 | R_SM0402 | RESISTOR; 0402; 22R; 1%; REEL 10000; | RC0402FR-0722RL | YAGEO (PHYCOMP) | Farnell | 1117301
47 | 5 | R130 R131 R132 R133 R134 | R_SM0402 | RESISTOR; 0402; 47R; 1%; REEL 10000; | RC0402FR-0747RL | YAGEO (PHYCOMP) | Farnell | 1117311
49.9 | 1 | R69 | R_SM0402 | RESISTOR; 0402; 1%; 49R9; | MCR01MRTF49R9 | ROHM Semiconductor | Digi-Key | RHM49.9CDCT-ND |  | CRCW040249R9FKED
51 | 4 | R59 R60 R63 R64 | R_SM0402 | RESISTOR; 0402; 0.063W; 1%; 51R; | RC0402FR-0751RL | YAGEO (PHYCOMP) | Farnell | 1458803RL
390 | 1 | R35 | R_SM0402 | RESISTOR; RC32H; 0402; 390R; | RC0402FR-07390RL | YAGEO (PHYCOMP) | Digi-Key | 311-390LRCT-ND |  | ERJ-2RKF3900X
470 | 1 | R43 | R_SM0402 | RESISTOR; RC32H; 0402; 470R; | RC0402FR-07470RL | YAGEO (PHYCOMP) | Digi-Key | 311-470LRCT-ND |  | ERJ-2RKF4700X
820 | 2 | R31 R33 | R_SM0402 | RES 820 OHM 1/16W 1% 0402 SMD | RC0402FR-07820RL | YAGEO (PHYCOMP) | Digi-Key | 311-820LRCT-ND
1K2 | 2 | R30 R32 | R_SM0402 | RES 1.2K OHM 1/16W 1% 0402 SMD | RC0402FR-071K2L | YAGEO (PHYCOMP) | Digi-Key | 311-1.20KLRCT-ND |  | MCR01MRTF1201
6K8 | 1 | R36 | R_SM0402 | RES 6.8K OHM 1/16W 1% 0402 SMD | RC0402FR-076K8L | YAGEO (PHYCOMP) | Digi-Key | 311-6.80KLRCT-ND |  | MCR01MRTF6801
10K | 6 | R83 R84 R85 R94 R96 R98 | R_SM0402 | RES 10K OHM 1/16W 1% 0402 SMD | RC0402FR-0710KL | YAGEO (PHYCOMP) | Digi-Key | 311-10.0KLRCT-ND |  | MCR01MRTF1002
10K | 1 | R95 | R_SM0402 | RES 10K OHM 1/16W 1% 0402 SMD | RC0402FR-0710KL | YAGEO (PHYCOMP) | Digi-Key | 311-10.0KLRCT-ND | NOFIT | MCR01MRTF1002
12K | 1 | R34 | R_SM0402 | RES 12K OHM 1/16W 1% 0402 SMD | RC0402FR-0712KL | YAGEO (PHYCOMP) | Digi-Key | 311-12.0KLRCT-ND |  | MCR01MRTF1202
1M | 3 | R2 R3 R50 | R_SM0402 | RESISTOR; THICK FILM; 1MOHM; 62.5mW; 1%; | RC0402FR-071ML | YAGEO | Farnell | 2127667
100MHz/600/0.2A | 16 | R6…R11 R13...R15 R19…R22 R37 R40 R87 | R_SM0402 | FERRITE BEAD; 600R; 0.25A; 0402; | 7427927161 | WURTH ELEKTRONIK | Farnell | 1961693
100MHz/60/1A | 3 | R41 R211 R215 | R_SM0805 | FERRITE BEAD; 0805; 60 OHM; | MMZ2012Y600B | TDK | Farnell | 1669733
TC1-1-13MA+ | 1 | T1 | TC1-1-13MA+ | RF Transformer; 4.5 - 3000 MHz; RF Power 0.25 Watt; Ratio 1:1; 50 Ohm; | TC1-1-13MA+ | Mini-Circuits | Minicircuits | TC1-1-13MA+
TC4-25X+ | 1 | T2 | TC1-1-13MA+ | RF Transformer; 500 - 2500 MHz; RF Power 0.25 Watt; Ratio 1:4; 50 Ohm; | TC4-25X+ | Mini-Circuits | Minicircuits | TC4-25X+
CONN_HROSE_FX10A-80P8 | 1 | X3 | FX10A-80P8 | CONN HEADER 80POS W/O POST SMD | FX10B-80P/8-SV1(71) | Hirose Electric | Digi-Key | H11228-ND
MMCX8400-0000 | 1 | X8 | MMCX | CON:MMCX Jack PCB Mount 50 Ohm | MMCX8400-0000 | JYEBAO | East Coast Microwave Dist | East Coast Microwave Dist | NOFIT
5-146285-2 | 1 | X2 | pinhead2 | BOARD-BOARD CONNECTOR HEADER; 2WAY; 1ROW; | 5-146285-2 | TE CONNECTIVITY / AMP | Farnell | 1341684 | NOFIT
CONN_6 | 1 | X9 | pinhead6 | Headers & Wire Housings 06 MODII HDR SRST B/A W/HD; | 104345-4 | TE Connectivity | TTI | 104345-4 | NOFIT
SMA8401-0000 | 2 | X6 X7 | SMA | SMA end launch jack medium version PCB Connector | LTI-SASF55MGT | Lighthorse Technologies | rfconnectors.com | LTI-SASF55MGT |  | SMA-J-P-H-ST-EM1-ND
5-104348-3 | 2 | X4 X5 | VR_pinhead5 | .100 inch AMPMODU Headers; RIGHT ANGLE; 5WAY; | 5-104348-3 | TE Connectivity | TTI | 5-104348-3 | NOFIT

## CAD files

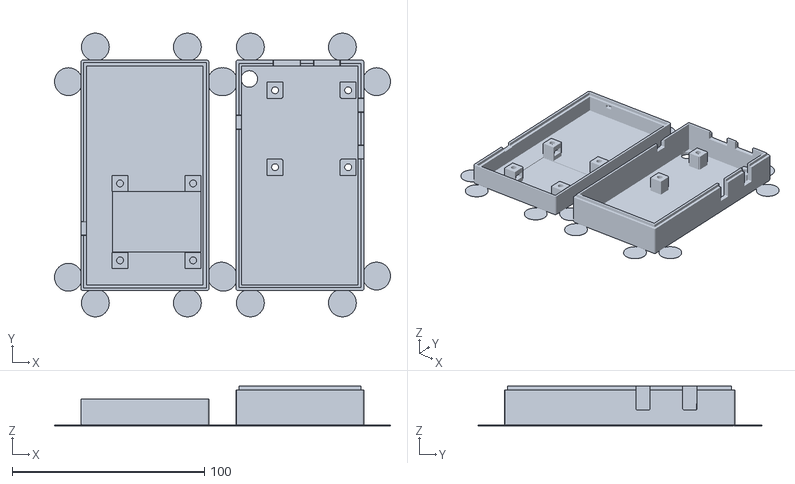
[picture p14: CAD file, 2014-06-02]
design/case/rasdr2-case-mfg.stl
174.7 x 147.6 x 20.6

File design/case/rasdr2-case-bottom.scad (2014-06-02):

difference() {
  difference() {
    difference() {
      difference() {
        difference() {
          intersection() {
            difference() {
              difference() {
                difference() {
                  difference() {
                    difference() {
                      union() {
                        difference() {
                          union() {
                            difference() {
                              union() {
                                difference() {
                                  union() {
                                    difference() {
                                      translate(v=[-3.300, -3.300, 0.000]) {
                                      rotate([-180.000,-180.000,-180.000]){
                                        cube(size=[66.600, 119.820, 12.000], center=false);
                                      } // End rotate
                                      } // End translate
                                      translate(v=[-0.300, -0.300, 2.000]) {
                                      rotate([-180.000,-180.000,-180.000]){
                                        cube(size=[60.600, 113.820, 10.100], center=false);
                                      } // End rotate
                                      } // End translate
                                    } // End difference
                                    difference() {
                                      translate(v=[-3.300, -3.300, 11.900]) {
                                      rotate([-180.000,-180.000,-180.000]){
                                        cube(size=[66.600, 119.820, 2.000], center=false);
                                      } // End rotate
                                      } // End translate
                                      translate(v=[-1.950, -1.950, 11.800]) {
                                      rotate([-180.000,-180.000,-180.000]){
                                        cube(size=[63.900, 117.120, 2.200], center=false);
                                      } // End rotate
                                      } // End translate
                                    } // End difference
                                    translate(v=[12.880, 48.200, 0.000]) {
                                    rotate([-180.000,-180.000,-180.000]){
                                      cube(size=[8.400, 8.400, 12.000], center=false);
                                    } // End rotate
                                    } // End translate
                                  } // End union
                                  translate(v=[17.080, 52.400, 2.000]) {
                                  rotate([-180.000,-180.000,-180.000]){
                                    cylinder(h=10.100, r1=1.800, r2=1.800, $fn=32, center=false);
                                  } // End rotate
                                  } // End translate
                                } // End difference
                                translate(v=[50.880, 48.200, 0.000]) {
                                rotate([-180.000,-180.000,-180.000]){
                                  cube(size=[8.400, 8.400, 12.000], center=false);
                                } // End rotate
                                } // End translate
                              } // End union
                              translate(v=[55.080, 52.400, 2.000]) {
                              rotate([-180.000,-180.000,-180.000]){
                                cylinder(h=10.100, r1=1.800, r2=1.800, $fn=32, center=false);
                              } // End rotate
                              } // End translate
                            } // End difference
                            translate(v=[12.880, 8.200, 0.000]) {
                            rotate([-180.000,-180.000,-180.000]){
                              cube(size=[8.400, 8.400, 12.000], center=false);
                            } // End rotate
                            } // End translate
                          } // End union
                          translate(v=[17.080, 12.400, 2.000]) {
                          rotate([-180.000,-180.000,-180.000]){
                            cylinder(h=10.100, r1=1.800, r2=1.800, $fn=32, center=false);
                          } // End rotate
                          } // End translate
                        } // End difference
                        translate(v=[50.880, 8.200, 0.000]) {
                        rotate([-180.000,-180.000,-180.000]){
                          cube(size=[8.400, 8.400, 12.000], center=false);
                        } // End rotate
                        } // End translate
                      } // End union
                      translate(v=[55.080, 12.400, 2.000]) {
                      rotate([-180.000,-180.000,-180.000]){
                        cylinder(h=10.100, r1=1.800, r2=1.800, $fn=32, center=false);
                      } // End rotate
                      } // End translate
                    } // End difference
                    translate(v=[14.130, 49.400, 5.000]) {
                    rotate([-180.000,-180.000,-180.000]){
                      cube(size=[8.500, 6.000, 3.500], center=false);
                    } // End rotate
                    } // End translate
                  } // End difference
                  translate(v=[49.630, 49.400, 5.000]) {
                  rotate([-180.000,-180.000,-180.000]){
                    cube(size=[8.500, 6.000, 3.500], center=false);
                  } // End rotate
                  } // End translate
                } // End difference
                translate(v=[14.130, 9.400, 5.000]) {
                rotate([-180.000,-180.000,-180.000]){
                  cube(size=[8.500, 6.000, 3.500], center=false);
                } // End rotate
                } // End translate
              } // End difference
              translate(v=[49.630, 9.400, 5.000]) {
              rotate([-180.000,-180.000,-180.000]){
                cube(size=[8.500, 6.000, 3.500], center=false);
              } // End rotate
              } // End translate
            } // End difference
            hull() {
              translate(v=[62.300, 115.520, 31.600]) {
              rotate([-180.000,-180.000,-180.000]){
                sphere(r=1.000, $fn=20, center=true);
              } // End rotate
              } // End translate
              translate(v=[-2.300, 115.520, 31.600]) {
              rotate([-180.000,-180.000,-180.000]){
                sphere(r=1.000, $fn=20, center=true);
              } // End rotate
              } // End translate
              translate(v=[62.300, -2.300, 31.600]) {
              rotate([-180.000,-180.000,-180.000]){
                sphere(r=1.000, $fn=20, center=true);
              } // End rotate
              } // End translate
              translate(v=[-2.300, -2.300, 31.600]) {
              rotate([-180.000,-180.000,-180.000]){
                sphere(r=1.000, $fn=20, center=true);
              } // End rotate
              } // End translate
              translate(v=[62.300, 115.520, 1.000]) {
              rotate([-180.000,-180.000,-180.000]){
                sphere(r=1.000, $fn=20, center=true);
              } // End rotate
              } // End translate
              translate(v=[-2.300, 115.520, 1.000]) {
              rotate([-180.000,-180.000,-180.000]){
                sphere(r=1.000, $fn=20, center=true);
              } // End rotate
              } // End translate
              translate(v=[62.300, -2.300, 1.000]) {
              rotate([-180.000,-180.000,-180.000]){
                sphere(r=1.000, $fn=20, center=true);
              } // End rotate
              } // End translate
              translate(v=[-2.300, -2.300, 1.000]) {
              rotate([-180.000,-180.000,-180.000]){
                sphere(r=1.000, $fn=20, center=true);
              } // End rotate
              } // End translate
            } // End hull
          } // End intersection
          hull() {
            translate(v=[16.500, 113.120, 10.300]) {
            rotate([90.000,-180.000,-180.000]){
              cylinder(h=3.500, r1=0.500, r2=0.500, $fn=32, center=false);
            } // End rotate
            } // End translate
            translate(v=[13.300, 113.120, 10.300]) {
            rotate([90.000,-180.000,-180.000]){
              cylinder(h=3.500, r1=0.500, r2=0.500, $fn=32, center=false);
            } // End rotate
            } // End translate
            translate(v=[13.300, 113.120, 9.100]) {
            rotate([90.000,-180.000,-180.000]){
              cylinder(h=3.500, r1=0.500, r2=0.500, $fn=32, center=false);
            } // End rotate
            } // End translate
            translate(v=[16.500, 113.120, 9.100]) {
            rotate([90.000,-180.000,-180.000]){
              cylinder(h=3.500, r1=0.500, r2=0.500, $fn=32, center=false);
            } // End rotate
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

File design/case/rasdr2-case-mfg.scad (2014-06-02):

union() {
  difference() {
    difference() {
      difference() {
        difference() {
          difference() {
            intersection() {
              difference() {
                difference() {
                  difference() {
                    difference() {
                      difference() {
                        union() {
                          difference() {
                            union() {
                              difference() {
                                union() {
                                  difference() {
                                    union() {
                                      difference() {
                                        translate(v=[-3.300, -3.300, 0.000]) {
                                        rotate([-180.000,-180.000,-180.000]){
                                          cube(size=[66.600, 119.820, 12.000], center=false);
                                        } // End rotate
                                        } // End translate
                                        translate(v=[-0.300, -0.300, 2.000]) {
                                        rotate([-180.000,-180.000,-180.000]){
                                          cube(size=[60.600, 113.820, 10.100], center=false);
                                        } // End rotate
                                        } // End translate
                                      } // End difference
                                      difference() {
                                        translate(v=[-3.300, -3.300, 11.900]) {
                                        rotate([-180.000,-180.000,-180.000]){
                                          cube(size=[66.600, 119.820, 2.000], center=false);
                                        } // End rotate
                                        } // End translate
                                        translate(v=[-1.950, -1.950, 11.800]) {
                                        rotate([-180.000,-180.000,-180.000]){
                                          cube(size=[63.900, 117.120, 2.200], center=false);
                                        } // End rotate
                                        } // End translate
                                      } // End difference
                                      translate(v=[12.880, 48.200, 0.000]) {
                                      rotate([-180.000,-180.000,-180.000]){
                                        cube(size=[8.400, 8.400, 12.000], center=false);
                                      } // End rotate
                                      } // End translate
                                    } // End union
                                    translate(v=[17.080, 52.400, 2.000]) {
                                    rotate([-180.000,-180.000,-180.000]){
                                      cylinder(h=10.100, r1=1.800, r2=1.800, $fn=32, center=false);
                                    } // End rotate
                                    } // End translate
                                  } // End difference
                                  translate(v=[50.880, 48.200, 0.000]) {
                                  rotate([-180.000,-180.000,-180.000]){
                                    cube(size=[8.400, 8.400, 12.000], center=false);
                                  } // End rotate
                                  } // End translate
                                } // End union
                                translate(v=[55.080, 52.400, 2.000]) {
                                rotate([-180.000,-180.000,-180.000]){
                                  cylinder(h=10.100, r1=1.800, r2=1.800, $fn=32, center=false);
                                } // End rotate
                                } // End translate
                              } // End difference
                              translate(v=[12.880, 8.200, 0.000]) {
                              rotate([-180.000,-180.000,-180.000]){
                                cube(size=[8.400, 8.400, 12.000], center=false);
                              } // End rotate
                              } // End translate
                            } // End union
                            translate(v=[17.080, 12.400, 2.000]) {
                            rotate([-180.000,-180.000,-180.000]){
                              cylinder(h=10.100, r1=1.800, r2=1.800, $fn=32, center=false);
                            } // End rotate
                            } // End translate
                          } // End difference
                          translate(v=[50.880, 8.200, 0.000]) {
                          rotate([-180.000,-180.000,-180.000]){
                            cube(size=[8.400, 8.400, 12.000], center=false);
                          } // End rotate
                          } // End translate
                        } // End union
                        translate(v=[55.080, 12.400, 2.000]) {
                        rotate([-180.000,-180.000,-180.000]){
                          cylinder(h=10.100, r1=1.800, r2=1.800, $fn=32, center=false);
                        } // End rotate
                        } // End translate
                      } // End difference
                      translate(v=[14.130, 49.400, 5.000]) {
                      rotate([-180.000,-180.000,-180.000]){
                        cube(size=[8.500, 6.000, 3.500], center=false);
                      } // End rotate
                      } // End translate
                    } // End difference
                    translate(v=[49.630, 49.400, 5.000]) {
                    rotate([-180.000,-180.000,-180.000]){
                      cube(size=[8.500, 6.000, 3.500], center=false);
                    } // End rotate
                    } // End translate
                  } // End difference
                  translate(v=[14.130, 9.400, 5.000]) {
                  rotate([-180.000,-180.000,-180.000]){
                    cube(size=[8.500, 6.000, 3.500], center=false);
                  } // End rotate
                  } // End translate
                } // End difference
                translate(v=[49.630, 9.400, 5.000]) {
                rotate([-180.000,-180.000,-180.000]){
                  cube(size=[8.500, 6.000, 3.500], center=false);
                } // End rotate
                } // End translate
              } // End difference
              hull() {
                translate(v=[62.300, 115.520, 31.600]) {
                rotate([-180.000,-180.000,-180.000]){
                  sphere(r=1.000, $fn=20, center=true);
                } // End rotate
                } // End translate
                translate(v=[-2.300, 115.520, 31.600]) {
                rotate([-180.000,-180.000,-180.000]){
                  sphere(r=1.000, $fn=20, center=true);
                } // End rotate
                } // End translate
                translate(v=[62.300, -2.300, 31.600]) {
                rotate([-180.000,-180.000,-180.000]){
                  sphere(r=1.000, $fn=20, center=true);
                } // End rotate
                } // End translate
                translate(v=[-2.300, -2.300, 31.600]) {
                rotate([-180.000,-180.000,-180.000]){
                  sphere(r=1.000, $fn=20, center=true);
                } // End rotate
                } // End translate
                translate(v=[62.300, 115.520, 1.000]) {
                rotate([-180.000,-180.000,-180.000]){
                  sphere(r=1.000, $fn=20, center=true);
                } // End rotate
                } // End translate
                translate(v=[-2.300, 115.520, 1.000]) {
                rotate([-180.000,-180.000,-180.000]){
                  sphere(r=1.000, $fn=20, center=true);
                } // End rotate
                } // End translate
                translate(v=[62.300, -2.300, 1.000]) {
                rotate([-180.000,-180.000,-180.000]){
                  sphere(r=1.000, $fn=20, center=true);
                } // End rotate
                } // End translate
                translate(v=[-2.300, -2.300, 1.000]) {
                rotate([-180.000,-180.000,-180.000]){
                  sphere(r=1.000, $fn=20, center=true);
                } // End rotate
                } // End translate
              } // End hull
            } // End intersection
            hull() {
              translate(v=[16.500, 113.120, 10.300]) {
              rotate([90.000,-180.000,-180.000]){
                cylinder(h=3.500, r1=0.500, r2=0.500, $fn=32, center=false);
              } // End rotate
              } // End translate
              translate(v=[13.300, 113.120, 10.300]) {
              rotate([90.000,-180.000,-180.000]){
                cylinder(h=3.500, r1=0.500, r2=0.500, $fn=32, center=false);
              } // End rotate
              } // End translate
              translate(v=[13.300, 113.120, 9.100]) {
              rotate([90.000,-180.000,-180.000]){
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

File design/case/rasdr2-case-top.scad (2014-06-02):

translate(v=[0.000, 113.220, 0.000]) {
rotate([-180.000,-180.000,-180.000]){
  scale(v=[1.000, -1.000, 1.000]) {
    difference() {
      difference() {
        difference() {
          difference() {
            difference() {
              difference() {
                difference() {
                  difference() {
                    difference() {
                      intersection() {
                        difference() {
                          union() {
                            difference() {
                              union() {
                                difference() {
                                  union() {
                                    difference() {
                                      union() {
                                        difference() {
                                          translate(v=[-3.300, -3.300, 0.000]) {
                                          rotate([-180.000,-180.000,-180.000]){
                                            cube(size=[66.600, 119.820, 18.700], center=false);
                                          } // End rotate
                                          } // End translate
                                          translate(v=[-0.300, -0.300, 2.000]) {
                                          rotate([-180.000,-180.000,-180.000]){
                                            cube(size=[60.600, 113.820, 16.800], center=false);
                                          } // End rotate
                                          } // End translate
                                        } // End difference
                                        difference() {
                                          translate(v=[-1.650, -1.650, 18.600]) {
                                          rotate([-180.000,-180.000,-180.000]){
                                            cube(size=[63.300, 116.520, 2.000], center=false);
                                          } // End rotate
                                          } // End translate
                                          translate(v=[-0.300, -0.300, 18.500]) {
                                          rotate([-180.000,-180.000,-180.000]){
                                            cube(size=[60.600, 113.820, 2.200], center=false);
                                          } // End rotate
                                          } // End translate
                                        } // End difference
                                        translate(v=[12.880, 48.200, 0.000]) {
                                        rotate([-180.000,-180.000,-180.000]){
                                          cube(size=[8.400, 8.400, 18.700], center=false);
                                        } // End rotate
                                        } // End translate
                                      } // End union
                                      translate(v=[17.080, 52.400, 5.900]) {
                                      rotate([-180.000,-180.000,-180.000]){
                                        cylinder(h=12.900, r1=1.800, r2=1.800, $fn=32, center=false);
                                      } // End rotate
                                      } // End translate
                                      translate(v=[17.080, 52.400, -0.100]) {
                                      rotate([-180.000,-180.000,-180.000]){
                                        cylinder(h=6.100, r1=2.900, r2=2.900, $fn=32, center=false);
                                      } // End rotate
                                      } // End translate
                                    } // End difference
                                    translate(v=[50.880, 48.200, 0.000]) {
                                    rotate([-180.000,-180.000,-180.000]){
                                      cube(size=[8.400, 8.400, 18.700], center=false);
                                    } // End rotate
                                    } // End translate
                                  } // End union
                                  translate(v=[55.080, 52.400, 5.900]) {
                                  rotate([-180.000,-180.000,-180.000]){
                                    cylinder(h=12.900, r1=1.800, r2=1.800, $fn=32, center=false);
                                  } // End rotate
                                  } // End translate
                                  translate(v=[55.080, 52.400, -0.100]) {
                                  rotate([-180.000,-180.000,-180.000]){
                                    cylinder(h=6.100, r1=2.900, r2=2.900, $fn=32, center=false);
                                  } // End rotate
                                  } // End translate
                                } // End difference
                                translate(v=[12.880, 8.200, 0.000]) {
                                rotate([-180.000,-180.000,-180.000]){
                                  cube(size=[8.400, 8.400, 18.700], center=false);
                                } // End rotate
                                } // End translate
                              } // End union
                              translate(v=[17.080, 12.400, 5.900]) {
                              rotate([-180.000,-180.000,-180.000]){
                                cylinder(h=12.900, r1=1.800, r2=1.800, $fn=32, center=false);
                              } // End rotate
                              } // End translate
                              translate(v=[17.080, 12.400, -0.100]) {
                              rotate([-180.000,-180.000,-180.000]){
                                cylinder(h=6.100, r1=2.900, r2=2.900, $fn=32, center=false);
                              } // End rotate
                              } // End translate
                            } // End difference
                            translate(v=[50.880, 8.200, 0.000]) {
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

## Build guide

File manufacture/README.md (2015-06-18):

# Radio Astronomy Software Defined Receiver (RASDR) Components for Manufacture

RASDR-COMPONENTS
*RASDR2 hardware components consisting of DigiRED and MyriadRF modules*

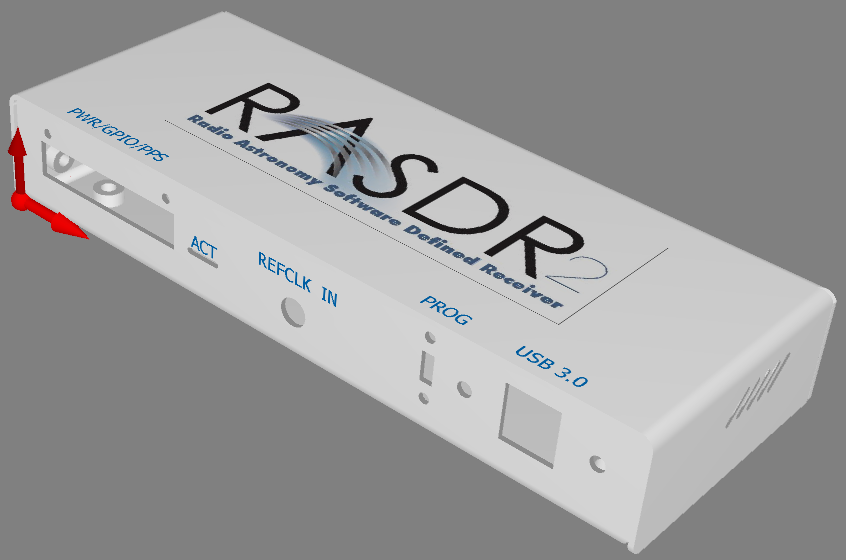
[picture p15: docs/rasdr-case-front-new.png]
RASDR-CASE

*RASDR2 case 3D model

## Directory Description ##

- **rasdr2-bom-and-components.xlsx** � contains a summary of all the components needed to build and assemble a complete RASDR device including all internal parts, case, connectors and cables.  A cost estimate of qty 10, 25 and 100 is given along with an extrapolation curve for numbers up to 1000.

- **DigiRED_v1r1** � contains the manufacturing files for the DigiRED USB digital interface board.  This board specifies a BOM that depopulates the TX side and USB to save cost.  It also specifies long-barrel SMA connectors to allow mounting to the custom case.

- **MyriadRF_v1r3e1** � contains the manufacturing files for the MyriadRF analog interface board.  This design is based on the via-off-pad, includes the resistors needed for proper operation with the DigiRED board, and has no vias less than 0.2mm to save cost.  It also specifies long-barrel SMA connectors to allow mounting to the custom case.

## Licensing ##
Unless otherwise specified, all hardware related designs and source artifacts are licensed under the  �Creative Commons Attribution 3.0 Unported�. To read the details of the license please review "license.html" or visit http://creativecommons.org/licenses/by/3.0/legalcode.

For specific information see the COPYING.MD file(s).

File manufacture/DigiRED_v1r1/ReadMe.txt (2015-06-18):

QUOTATION PACKAGE --- FOR MANUFACTURE
=====================================

Please quote the following (PCB+Assembly):
A) QTY=100,  Delivery=PROD, Turnkey, first article service requested
B) QTY=250,  Delivery=PROD, Turnkey, first article service requested
C) QTY=1000, Delivery=PROD, Turnkey, first article service requested

Please direct technical questions to:

Bogdan Vacaliuc
bvacaliuc@gmail.com, vacaliucb@ornl.gov
603-591-2458 cell

Please direct financial questions to:
Melinda Lord
Treasurer, Society of Amateur Radio Astronomers
treasurer@radio-astronomy.org, ap_guardian@yahoo.com

For CTS/Valpey components, contact:
Janet Cicero (jcicero@doveonline.com )
Dove Electronic Components
39 Research Way
East Setauket, NY 11733
Freephone: 1 800 232 XTAL 
Telephone: 1 631 689 7733
Fax: 1 631 689 7362
http://www.doveonline.com/

Board Description
-----------------

board designation           : DigiRED v1 RX
board version               : version 1, revision 1	
board type                  : Lead Free
board size                  : 59.0 mm x 62.0 mm
board thickness             : 1.6 mm +/- 10 %
board material              : FR4
number of layers            : 6
Gerber file format          : RS-274-X
Solder Mask                 : black TAIYO, both sides, halogen free.
Silkscreen                  : white epoxy ink, halogen free, both sides.

Top layer copper foil thickness	: 18 um
Dielectric thickness between Top layer and 2nd layer: 180 um
Dielectric between Top layer and 2nd layer relative permittivity (Er): 4.4

plating finish (both sides) : electroless nickel immersion gold (ENIG)
                              0.08-0.13 um of gold over
                              3.00-6.00 um of nickel
                              per IPC-4552 Amendment 1

Min track width 	    : 0.20 mm  
Min Via hole drill          : 0.20 mm  
Min pads and track clearance: 0.10 mm 

Important Notes
---------------

DRCs must be run on Gerber files before building boards.

All through hole vias may be plated shut.

Electrical test : 100 % netlist.

Boards are to be individually bagged.

Design software used:  KiCad

The BOM contains several NOFIT parts.  These have been carefully identified and do not need to be placed.  The schematic shows R135 and TCXO2 as 'NF'.  The BOM shows TCXO1 as 'NF'.  The BOM is correct.  I did not wish to modify the schematic at this time as there are no changes except for the BOM.

Controlled Impedance
--------------------

1.  90 Ohm differential microstrip (Top layer)
    FR4, 180 um, Er = 4.4, tand = 0.025, metal thickness 18 um
    track width 280 um

Board Stackup
-------------

Solder Paste Front              : DigiRED_v1-F_Paste.gbp
Silk Screen Front               : DigiRED_v1-F_SilkS.gto
Solder Mask Front               : DigiRED_v1-F_Mask.gts

1. Top Layer                    : DigiRED_v1-01-Front_Cu.gtl
2. GND Layer                    : DigiRED_v1-02-GND_Cu.gbr				
3. Inner Layer 1                : DigiRED_v1-03-Signal_1_Cu.gbr
4. Inner Layer 2                : DigiRED_v1-04-Signal_2_Cu.gbr
5. Power Layer                  : DigiRED_v1-05-Power_Cu.gbr
6. Bottom Layer                 : DigiRED_v1-06-Back_Cu.gbl

Solder Mask Back                : DigiRED_v1-B_Mask.gbs
Silk Screen Back                : DigiRED_v1-B_SilkS.gbo
Solder Paste Back               : DigiRED_v1-B_Paste.gbp

Additional Files
----------------

PCB edges                       : DigiRED_v1-Edge_Cuts.gbr
Drill map                       : DigiRED_v1-drl_map.pho
NC Drill file                   : DigiRED_v1.drl
Bill of Materials File          : DigiRED_v1_BOM.xls

Descriptive Layer Stack Up      : DigiRED_v1_PCB_Layer_Stack_Up.pdf

Schematics                      : DigiRED_v1_Schematics_v1r1.pdf
Component Positions Reference   : DigiRED_v1-all_pos.txt

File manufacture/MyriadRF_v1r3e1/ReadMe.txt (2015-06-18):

QUOTATION PACKAGE --- FOR MANUFACTURE

=====================================

Please quote the following (PCB+Assembly):

A) QTY=100,  Delivery=PROD, Turnkey, first article service requested
B) QTY=250,  Delivery=PROD, Turnkey, first article service requested
C) QTY=1000, Delivery=PROD, Turnkey, first article service requested

Please direct technical questions to:

Bogdan Vacaliuc

bvacaliuc@gmail.com, vacaliucb@ornl.gov

603-591-2458 cell

Please direct financial questions to:

Melinda Lord

Treasurer, Society of Amateur Radio Astronomers

treasurer@radio-astronomy.org, ap_guardian@yahoo.com

For Lime Microsystems components, contact:

Richardson RFPD

40W267 Keslinger Road

LaFox, IL 60147-0307

United States of America

Tel: +1 (630) 208-2700

Fax: +1 (630) 208-2662

www.richardsonrfpd.com

Board Description
-----------------

board designation           : MYRIAD RF Via Off Pad 
board version		    : version 1, revision 3, eco 1
board type                  : Lead Free
board size                  : 48.0 mm x 46.0 mm
board thickness             : 1.6 mm +/- 10 %
board material              : FR4
number of layers            : 6

Top layer copper foil thickness: 17.5 um
Dielectric thickness between Top layer and 2nd layer: 173 um (6.8 mils)
Dielectric between Top layer and 2nd layer relative permittivity (Er): 4.2

minimum finished hole size  :  200 um
minimum spacing             :  100 um
minimum track width         :  100 um

Gerber file format          : RS-274-X 

drill diameters             : finished hole

plating finish (both sides) : electroless nickel immersion gold (ENIG)
                              0.08-0.13 um of gold over
                              3.00-6.00 um of nickel
                              per IPC-4552 Amendment 1

Important Notes
---------------

DRCs must be run on Gerber files before building boards.

All through hole vias may be plated shut.

Solder mask : black TAIYO, both sides, halogen free.

Silkscreen : white epoxy ink, halogen free, both sides.

Electrical test : 100 % netlist.

Boards are to be individually bagged.

Basic grid increment is 5 um.

Design software used:  KiCad

The BOM contains several NOFIT parts.  These have been carefully identified and do not need to be placed.  

The BOM contains an EMI shield from Laird Technologies (BMI-S-204-F) that comes in two parts.  The part that is soldered onto the PCB should be fitted, but the upper part does not need to be attached, and may be provided in a parts bag separately.  Both parts should be obtained when purchasing parts.

Controlled Impedance
--------------------

  * 50 Ohm coated single ended microstrip (Top layer)
    FR4, 6.8 mil, Er = 4.2, tand = 0.025, metal thickness 17.5 um
    track width 310 um

Board Stackup
----------------

Solder Paste Front              : MYRIAD_RF-F_Paste.gtp
Silk Screen Front               : MYRIAD_RF-F_SilkS.gto
SolderMask Front                : MYRIAD_RF-F_Mask.gts

1. Top Layer                    : MYRIAD_RF-01-Front.gtl
2. Inner GND Layer              : MYRIAD_RF-02-Inner_GND.gbr

3. Inner Layer 1                : MYRIAD_RF-03-Inner_Analog_Signal.gbr
4. Inner Power Layer            : MYRIAD_RF-04-Inner_Power.gbr
5. Inner Layer 2                : MYRIAD_RF-05-Inner_Digital_Signal.gbr
6. Bottom Layer                 : MYRIAD_RF-06-Back.gbl

SolderMask Back                 : MYRIAD_RF-B_Mask.gbs
Silk Screen Back                : MYRIAD_RF-B_SilkS.gbo
Solder Paste Back               : MYRIAD_RF-B_Paste.gbp

Additional Files
----------------
PCB edges                       : MYRIAD_RF-Edge_Cuts.gbr
Drawings                        : MYRIAD_RF-Dwgs_User.gbr
Drill map                       : MYRIAD_RF-drl_map.pho
NC Drill file                   : MYRIAD_RF.drl
Bill of Materials File          : MYRIAD_RF_BOM.xls

Descriptive Layer Stack Up      : MYRIAD_RF_PCB_Layer_Stack_Up.pdf

Schematics                      : MYRIAD_RF_Schematics_v1r2.pdf

Component Positions Reference   : MYRIAD_RF-all_pos.txt

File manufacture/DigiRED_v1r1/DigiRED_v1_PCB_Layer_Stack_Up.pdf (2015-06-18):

# PCB Layer Stack-up

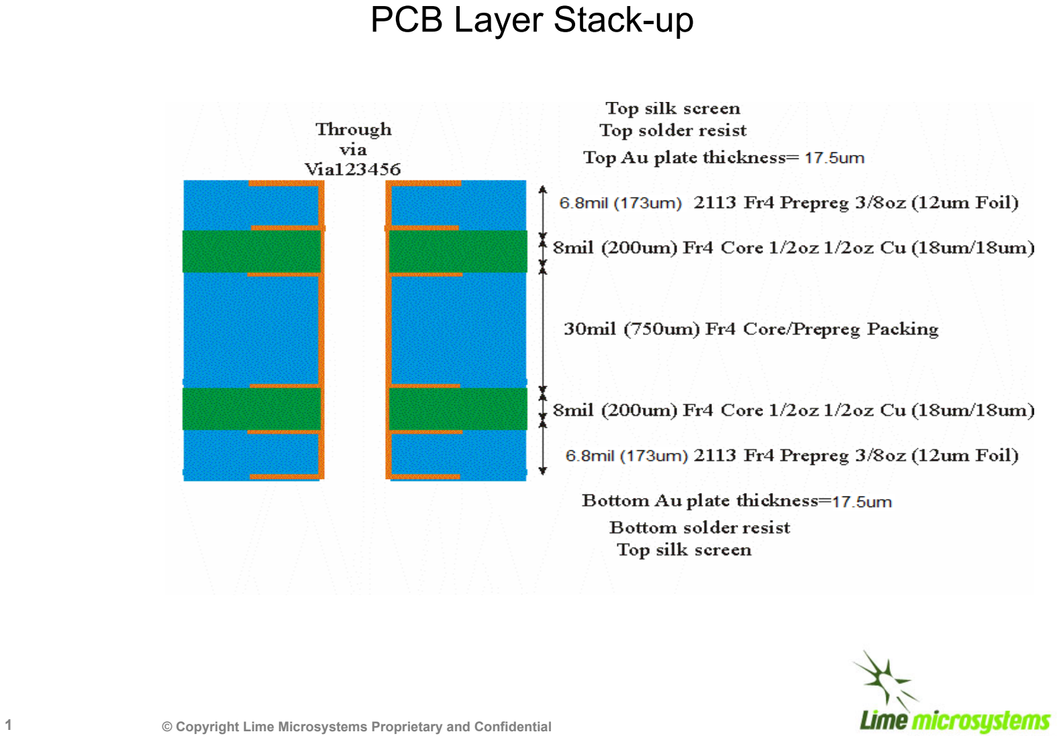
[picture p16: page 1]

1 © Copyright Lime Microsystems Proprietary and Confidential

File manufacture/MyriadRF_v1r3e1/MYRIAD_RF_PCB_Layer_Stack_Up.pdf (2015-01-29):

# PCB Layer Stack-up

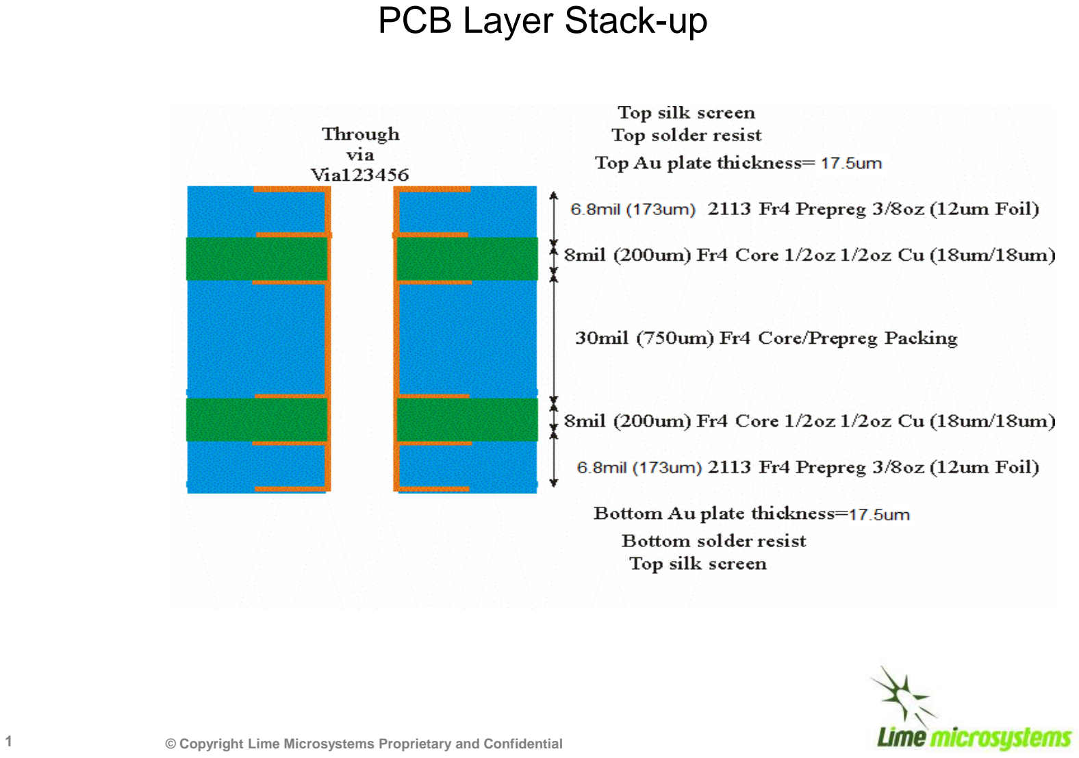
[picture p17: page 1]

1 © Copyright Lime Microsystems Proprietary and Confidential

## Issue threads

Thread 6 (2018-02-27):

### ISSUE TITLE
Question: manufacturing process

### ISSUE THREAD

**Issue by mahrud** [myriadrf/RASDR#6]
Open hardware files are provided, but I'm not sure what sort of facility I should be looking for to actually create them and how much it would cost. Would a big university have the equipment to manufacture this?

**Comment by bvacaliuc** [comment]
We provided a complete workup on manufacturing cost and presented it at the [2015 SARA annual conference](http://radio-astronomy.org/?q=node/208).

See this [spreadsheet](https://github.com/myriadrf/RASDR/blob/master/manufacture/rasdr2-bom-and-components.xlsx) for details.  We worked up quantity of 10, 25 and 100 units.  The spreadsheet contains part numbers and quotation numbers from our suppliers, [Advanced Assembly](http://aa-pcbassembly.com/) and [Protocase, Inc.](http://www.protocase.com/).

Our intent was to provide complete manufacturing documentation for turnkey production.  "Just add $$$...".  There is still some work to be done in assembling the components in the case, but that can be accomplished by eager (under)graduate students.  :)

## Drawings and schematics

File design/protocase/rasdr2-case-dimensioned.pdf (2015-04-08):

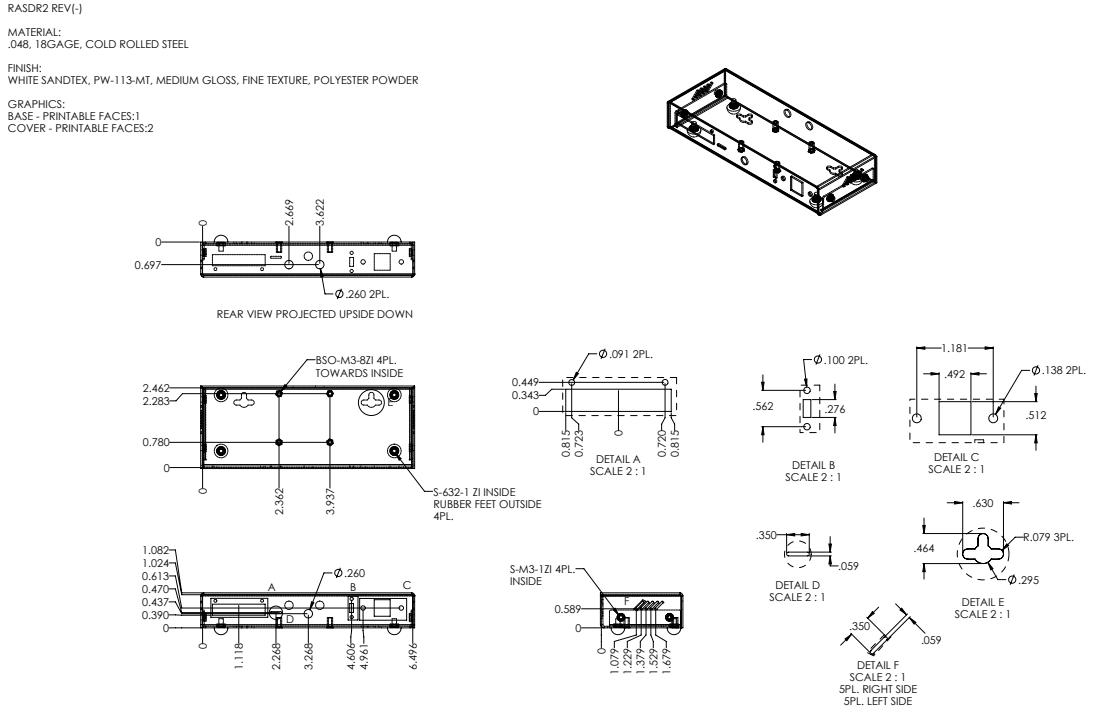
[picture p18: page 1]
BSO-M3-8ZI 4PL. TOWARDS INSIDE; DETAIL A SCALE 2 : 1; DETAIL B SCALE 2 : 1; DETAIL C SCALE 2 : 1; DETAIL D SCALE 2 : 1; DETAIL E SCALE 2 : 1; DETAIL F SCALE 2 : 1 5PL. RIGHT SIDE 5PL. LEFT SIDE

RASDR2 REV(-)
MATERIAL:
.048, 18GAGE, COLD ROLLED STEEL
FINISH:
WHITE SANDTEX, PW-113-MT, MEDIUM GLOSS, FINE TEXTURE, POLYESTER POWDER
GRAPHICS:
BASE - PRINTABLE FACES:1
COVER - PRINTABLE FACES:2

REAR VIEW PROJECTED UPSIDE DOWN

S-632-1 ZI INSIDE
RUBBER FEET OUTSIDE

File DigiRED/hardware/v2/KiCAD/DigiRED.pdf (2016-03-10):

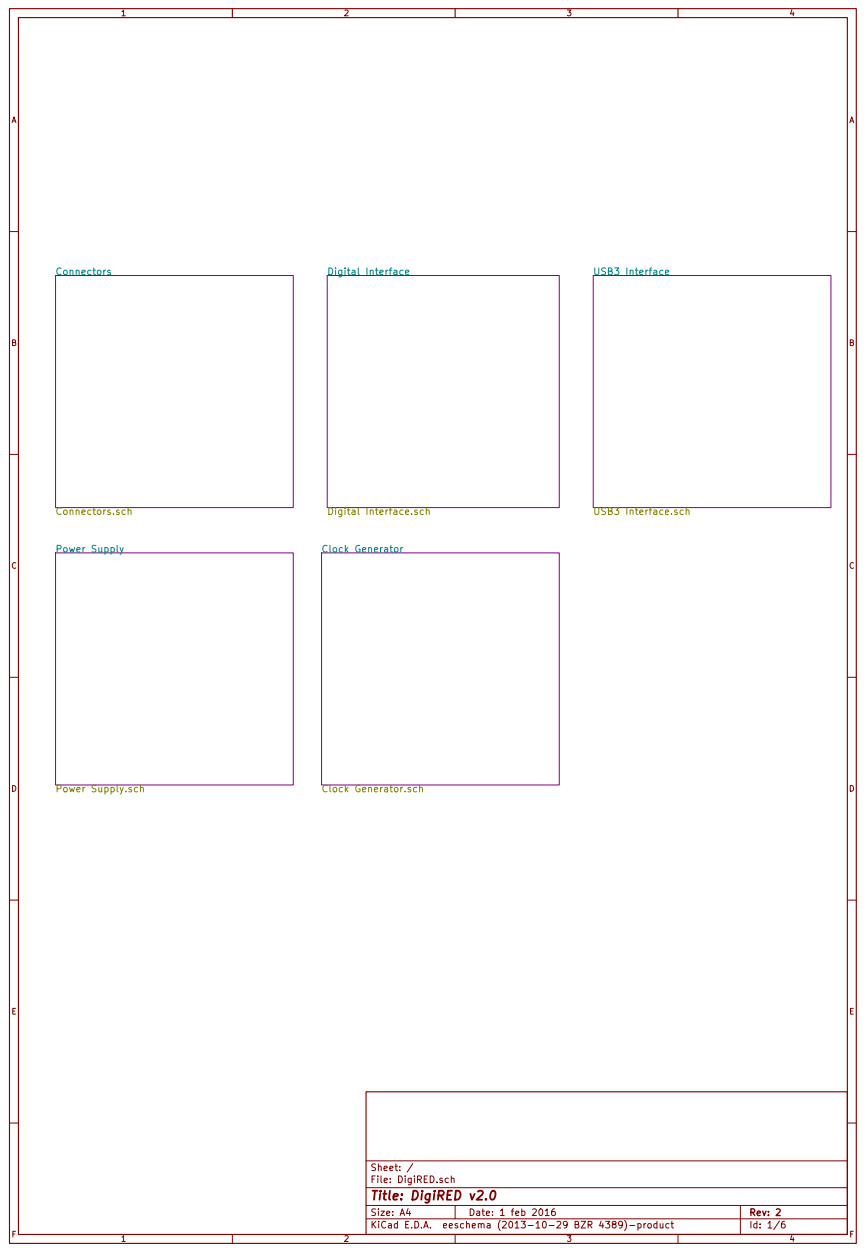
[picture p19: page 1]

File: DigiRED.sch Sheet: /
Id: 1/6 Title: DigiRED v2.0

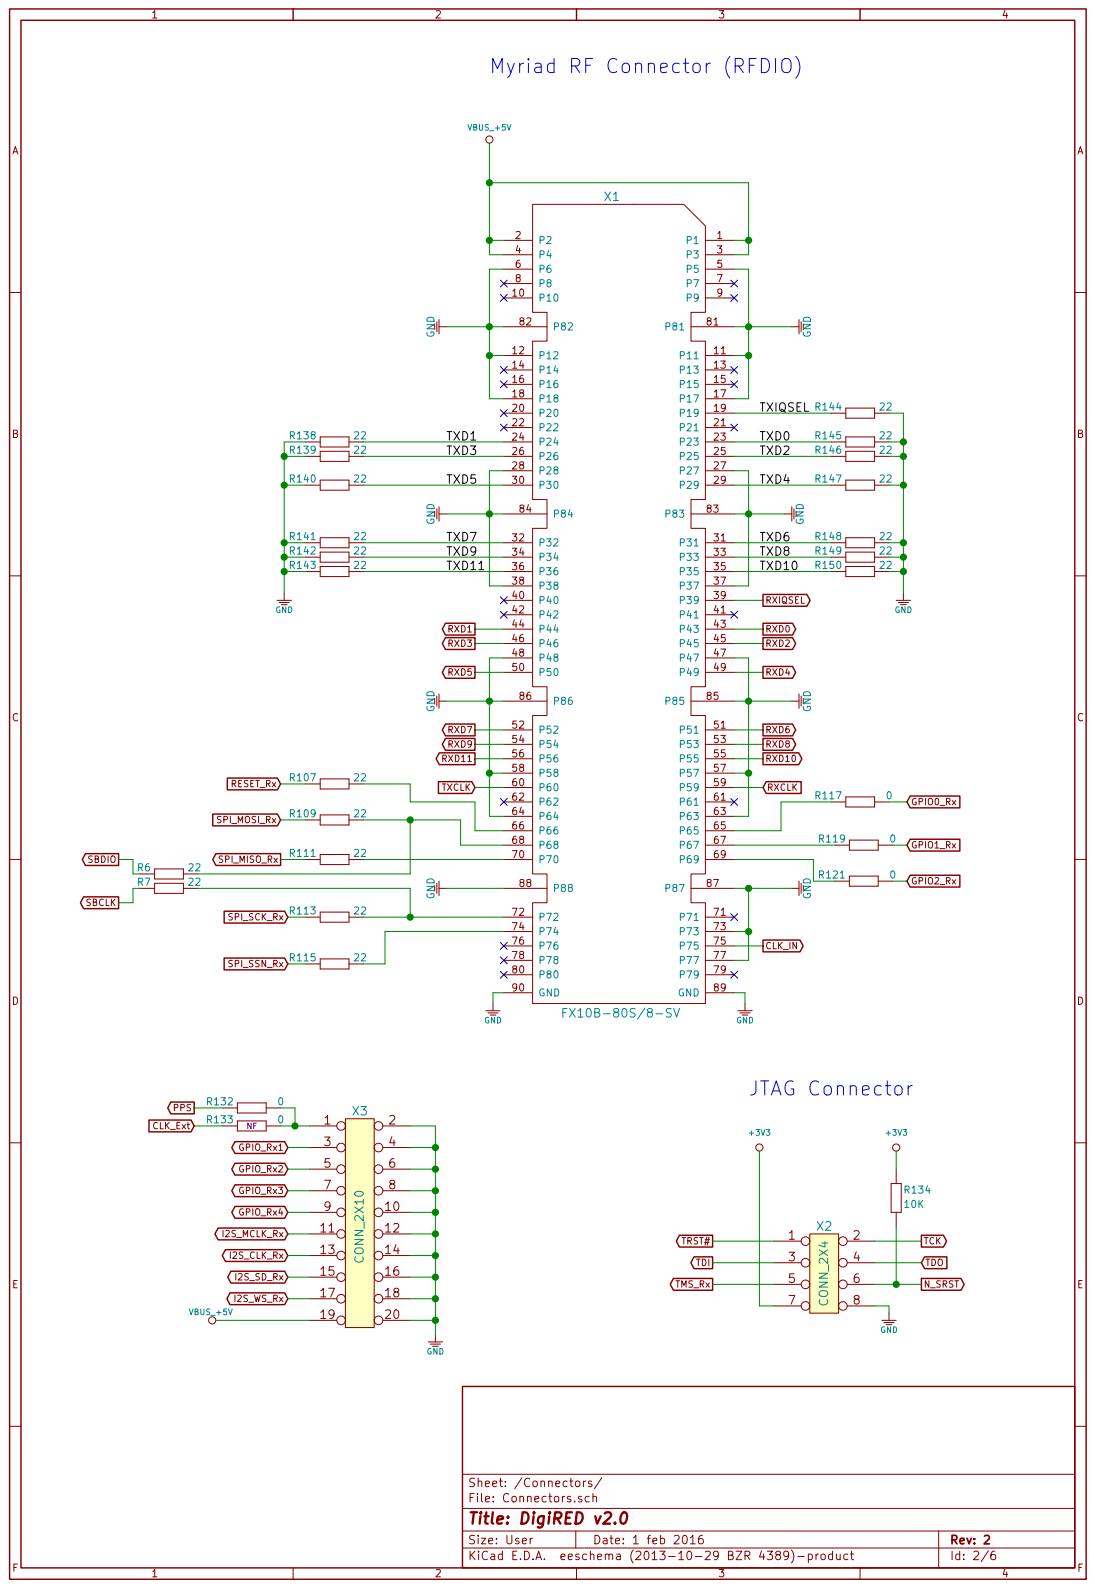
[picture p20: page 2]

File: Connectors.sch Sheet: /Connectors/
Id: 2/6 Title: DigiRED v2.0

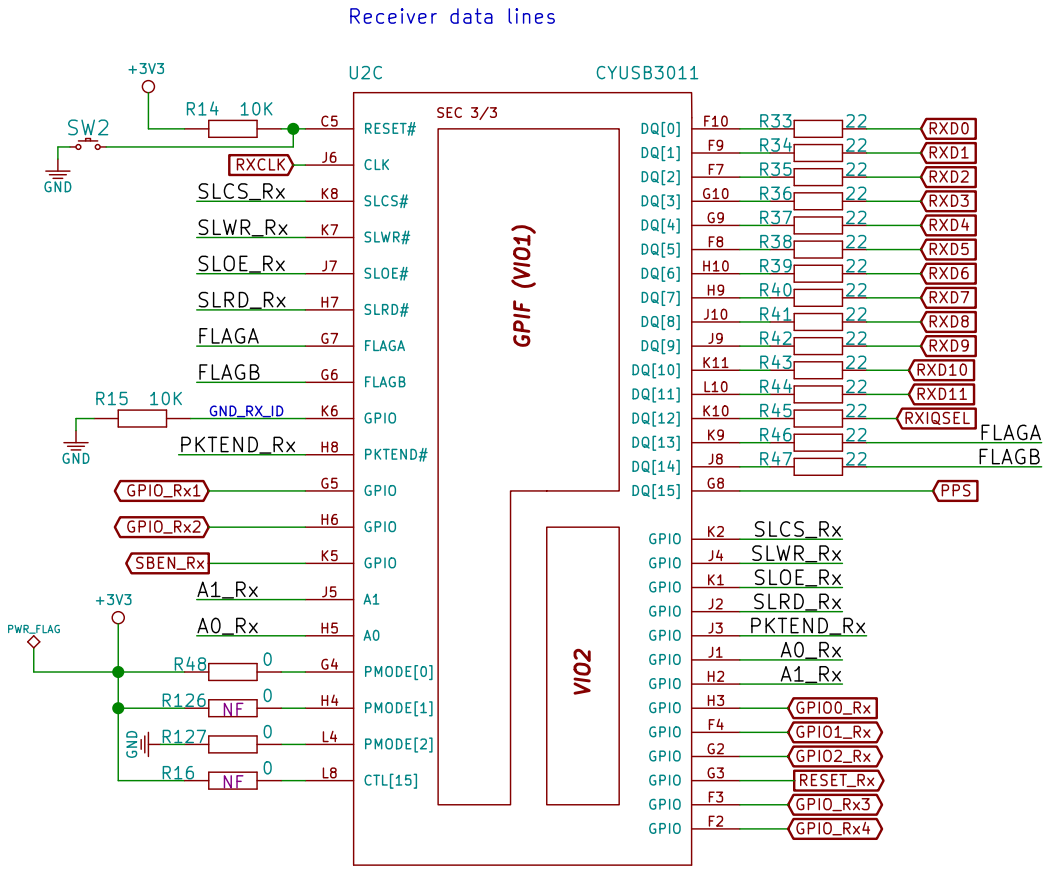
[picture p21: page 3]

Sheet: /Digital Interface/
File: Digital Interface.sch
Id: 3/6 Title: DigiRED v2.0

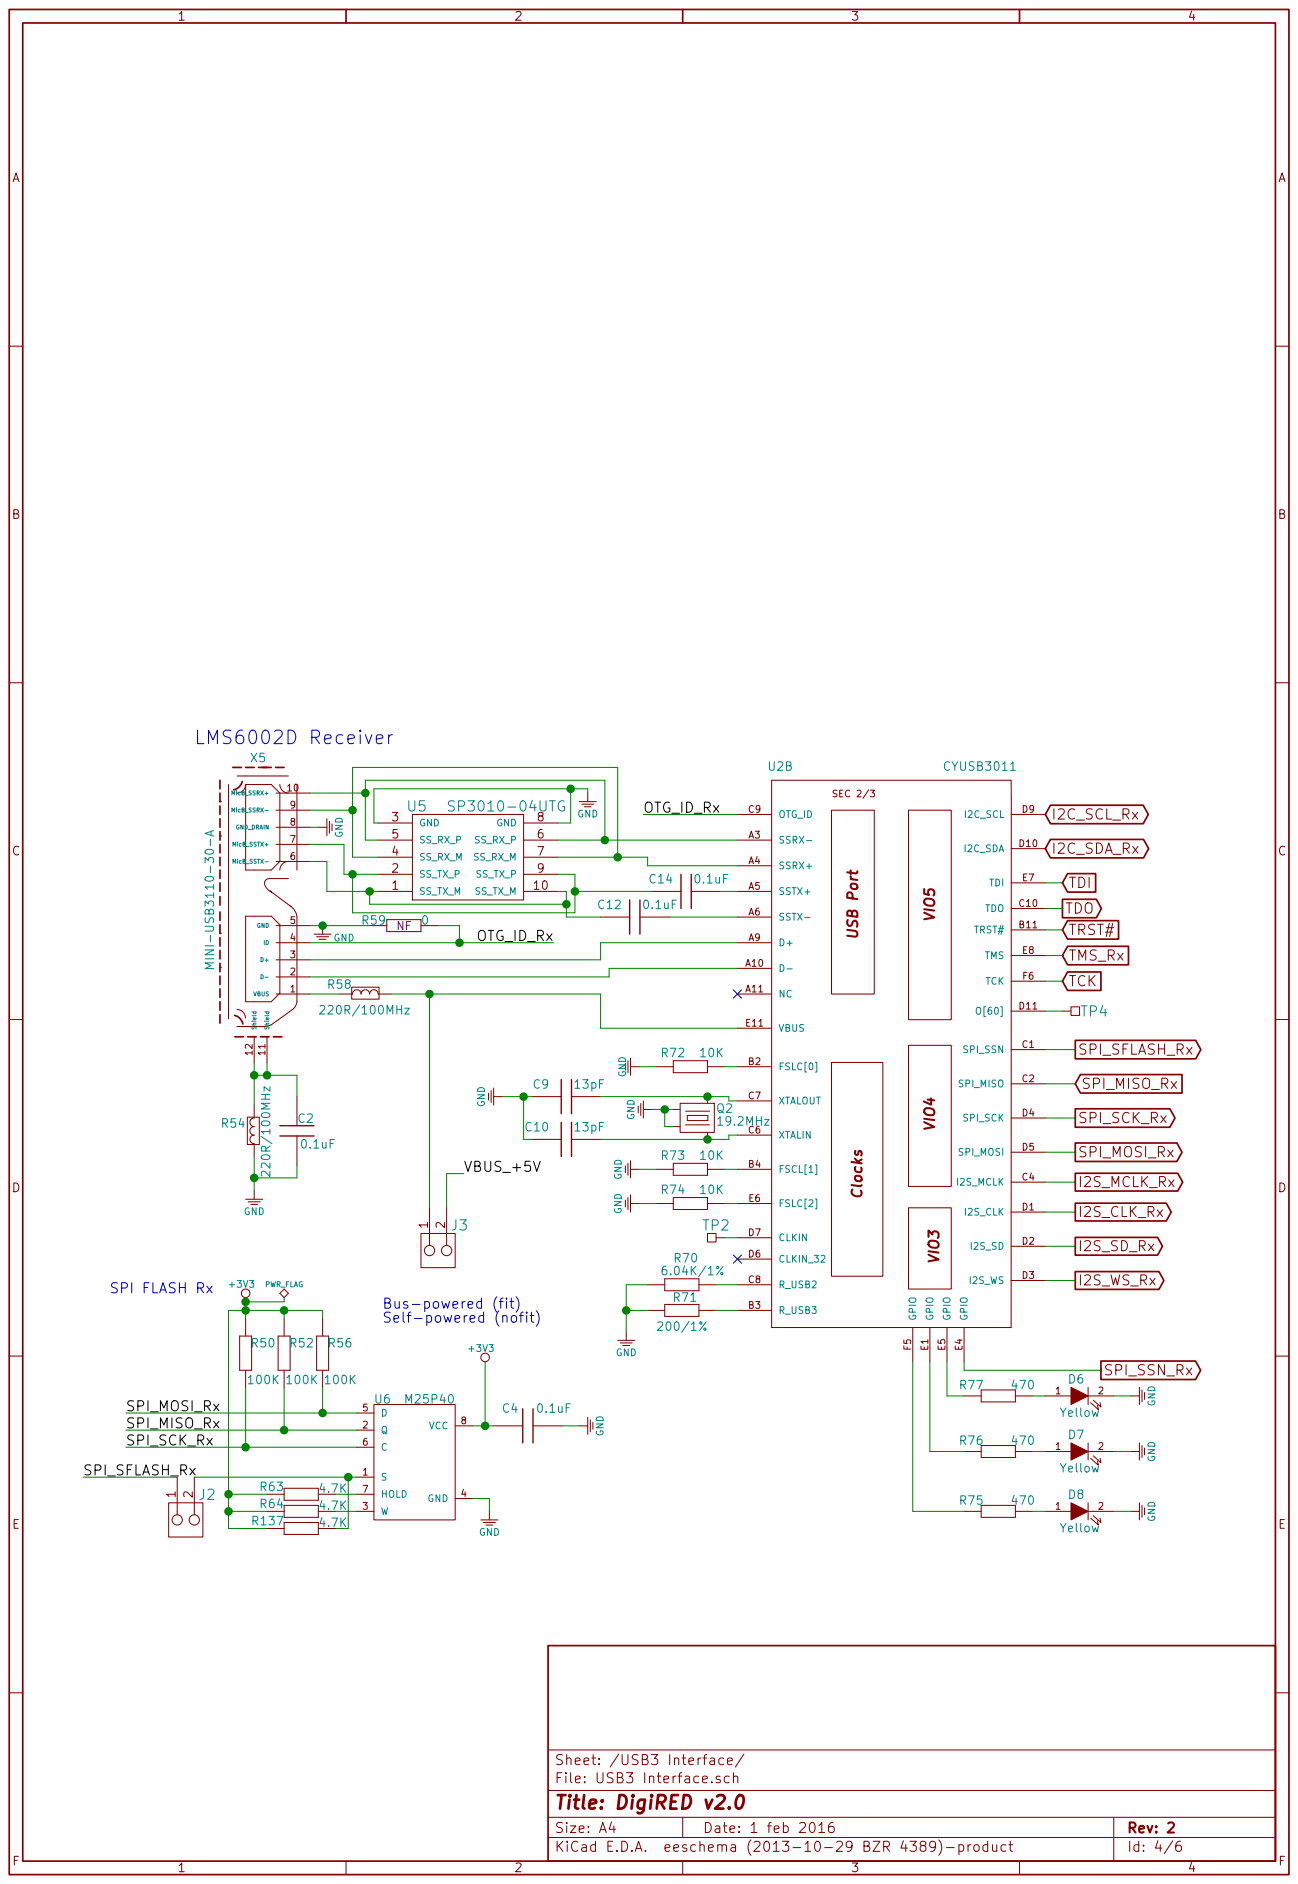
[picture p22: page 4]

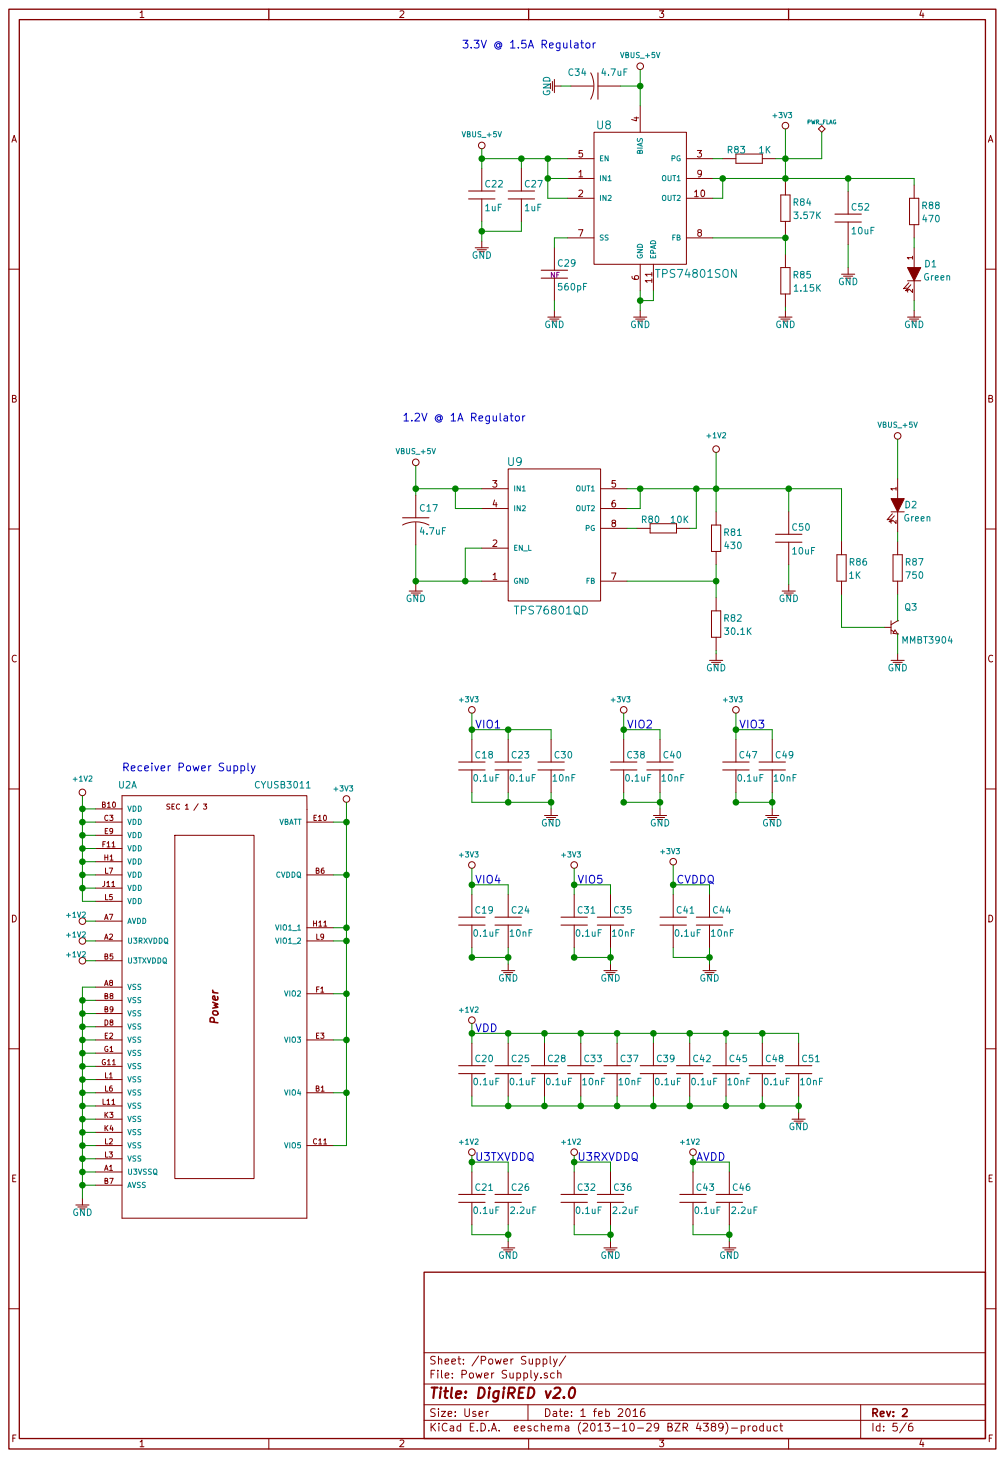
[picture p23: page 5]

Sheet: /Power Supply/
File: Power Supply.sch
Id: 5/6 Title: DigiRED v2.0

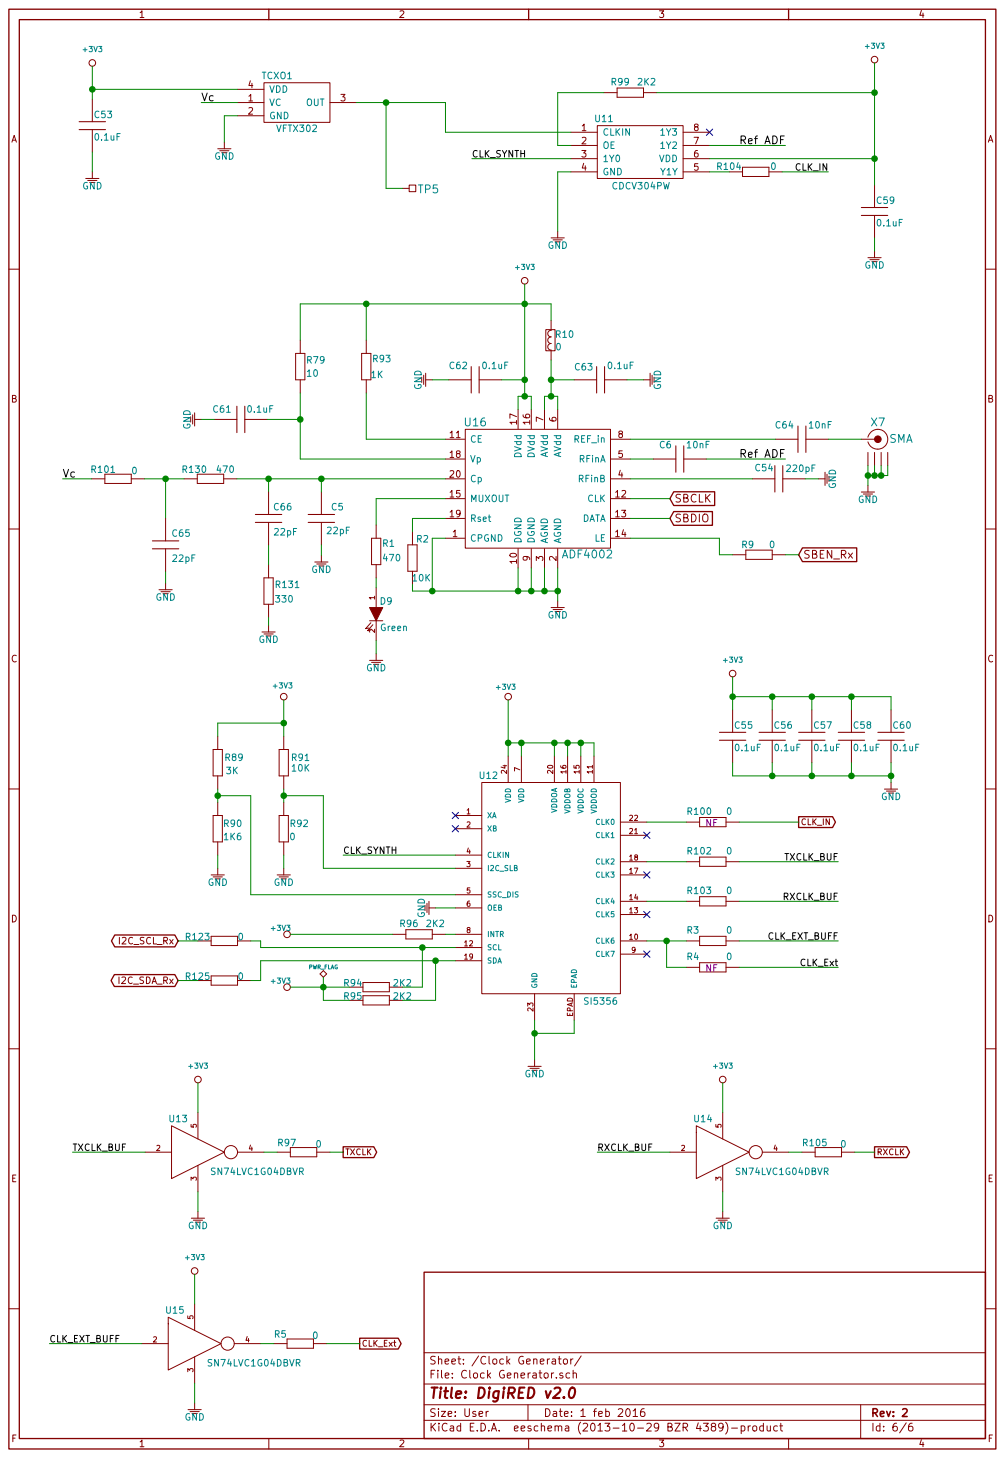
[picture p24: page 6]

1 2 D9Green GND GND GND GND Vc Ref ADF Ref ADF GND GND GND GND

File: Clock Generator.sch Sheet: /Clock Generator/
Id: 6/6 Title: DigiRED v2.0

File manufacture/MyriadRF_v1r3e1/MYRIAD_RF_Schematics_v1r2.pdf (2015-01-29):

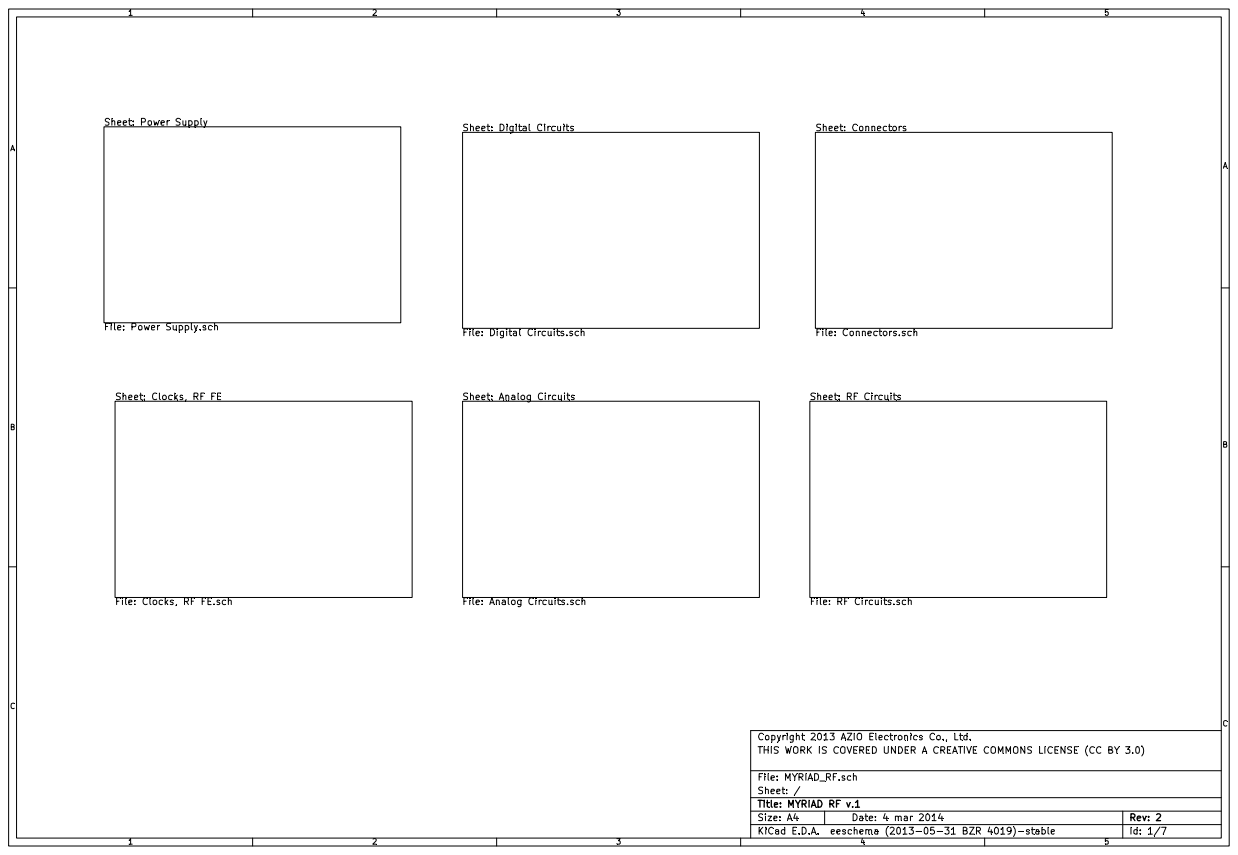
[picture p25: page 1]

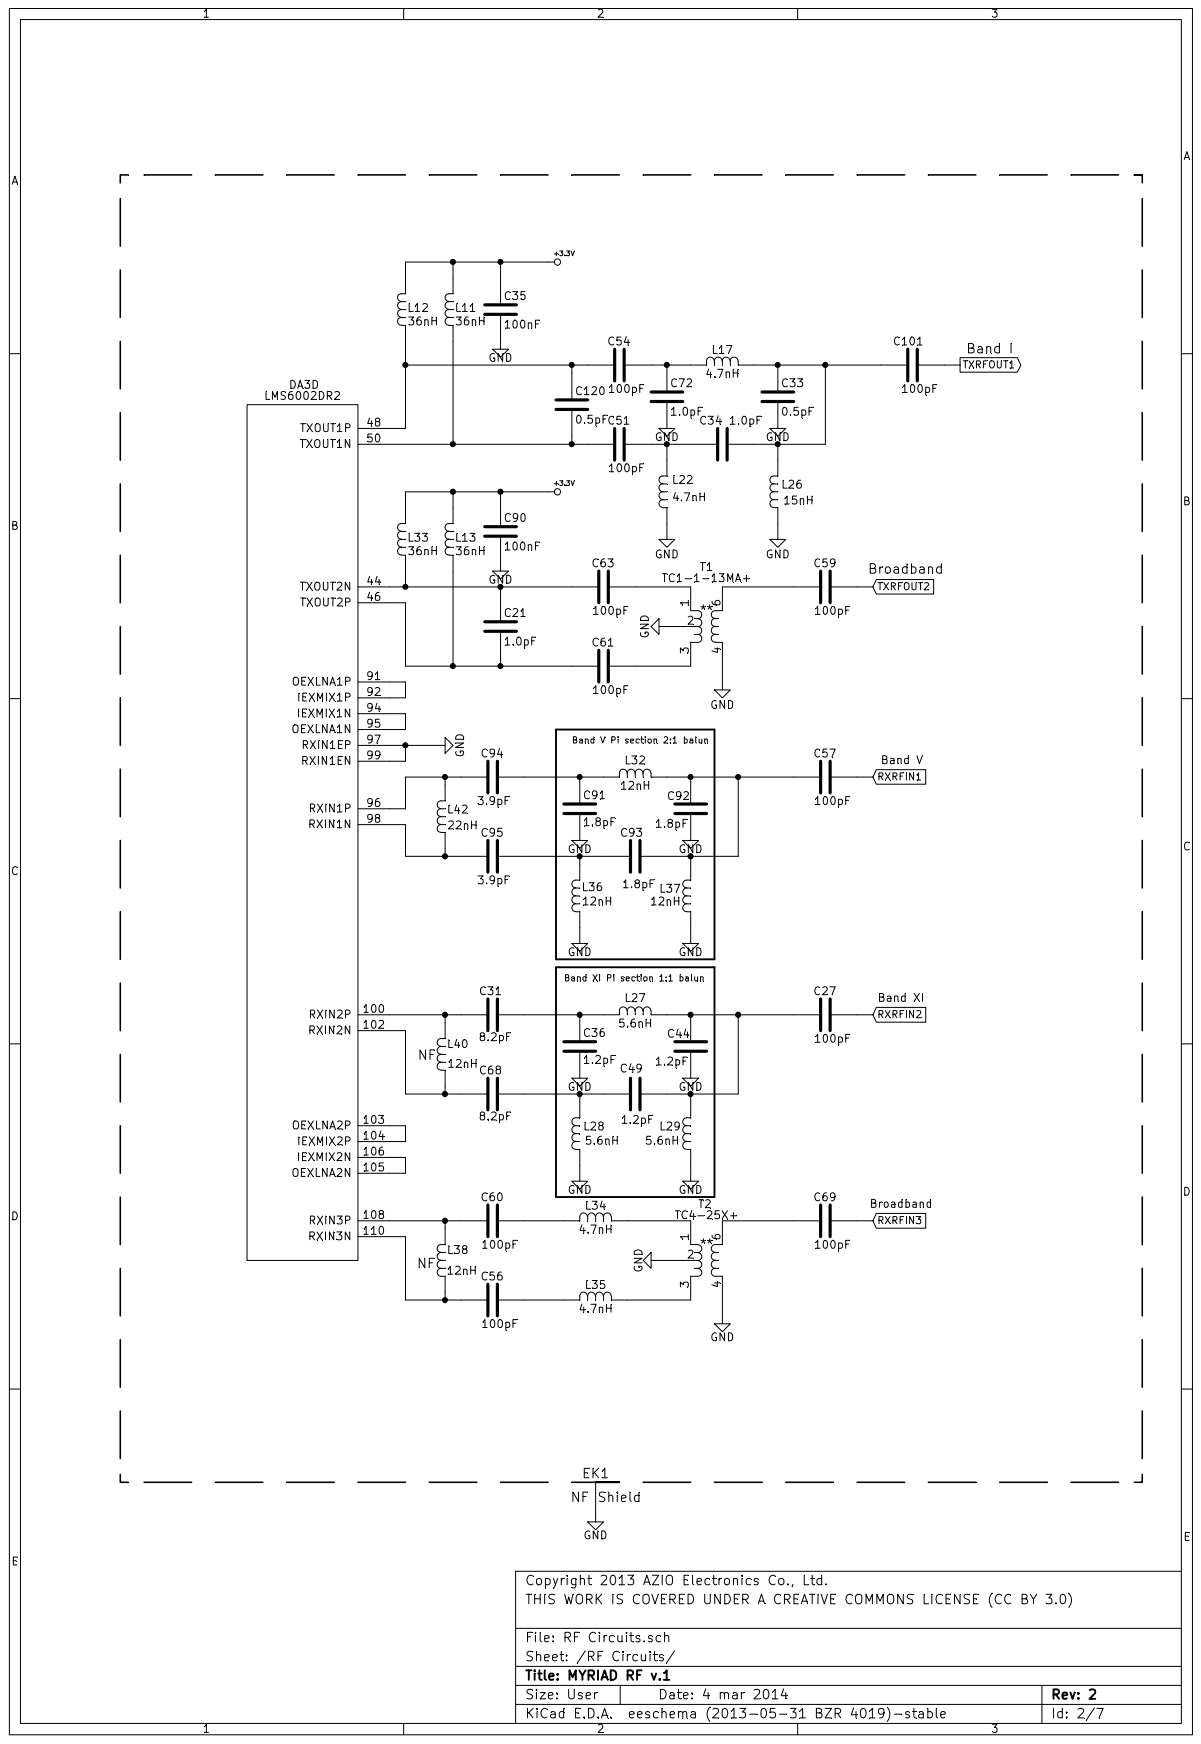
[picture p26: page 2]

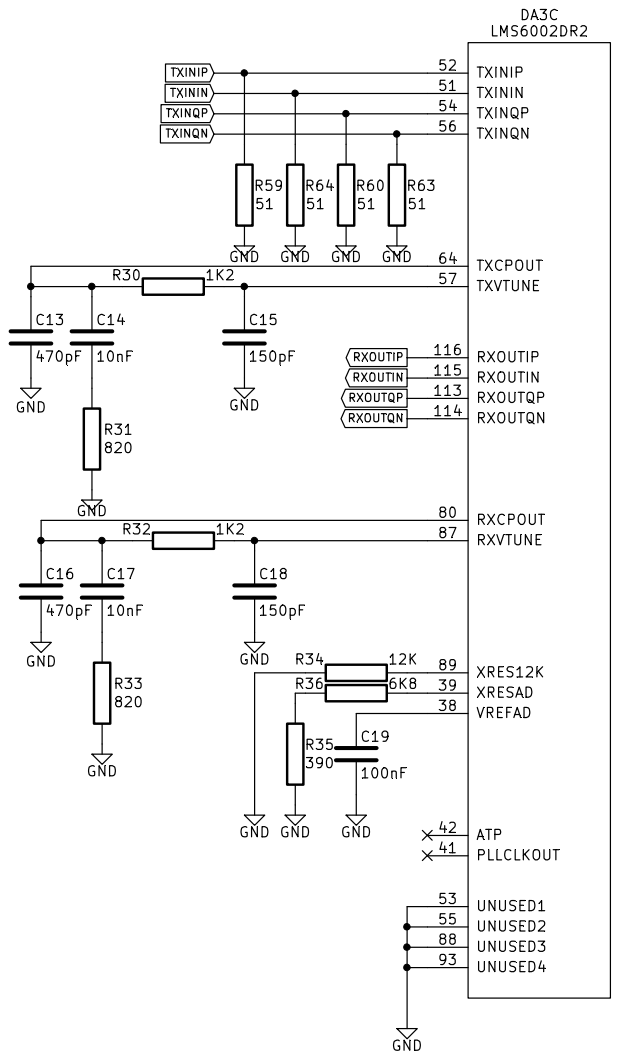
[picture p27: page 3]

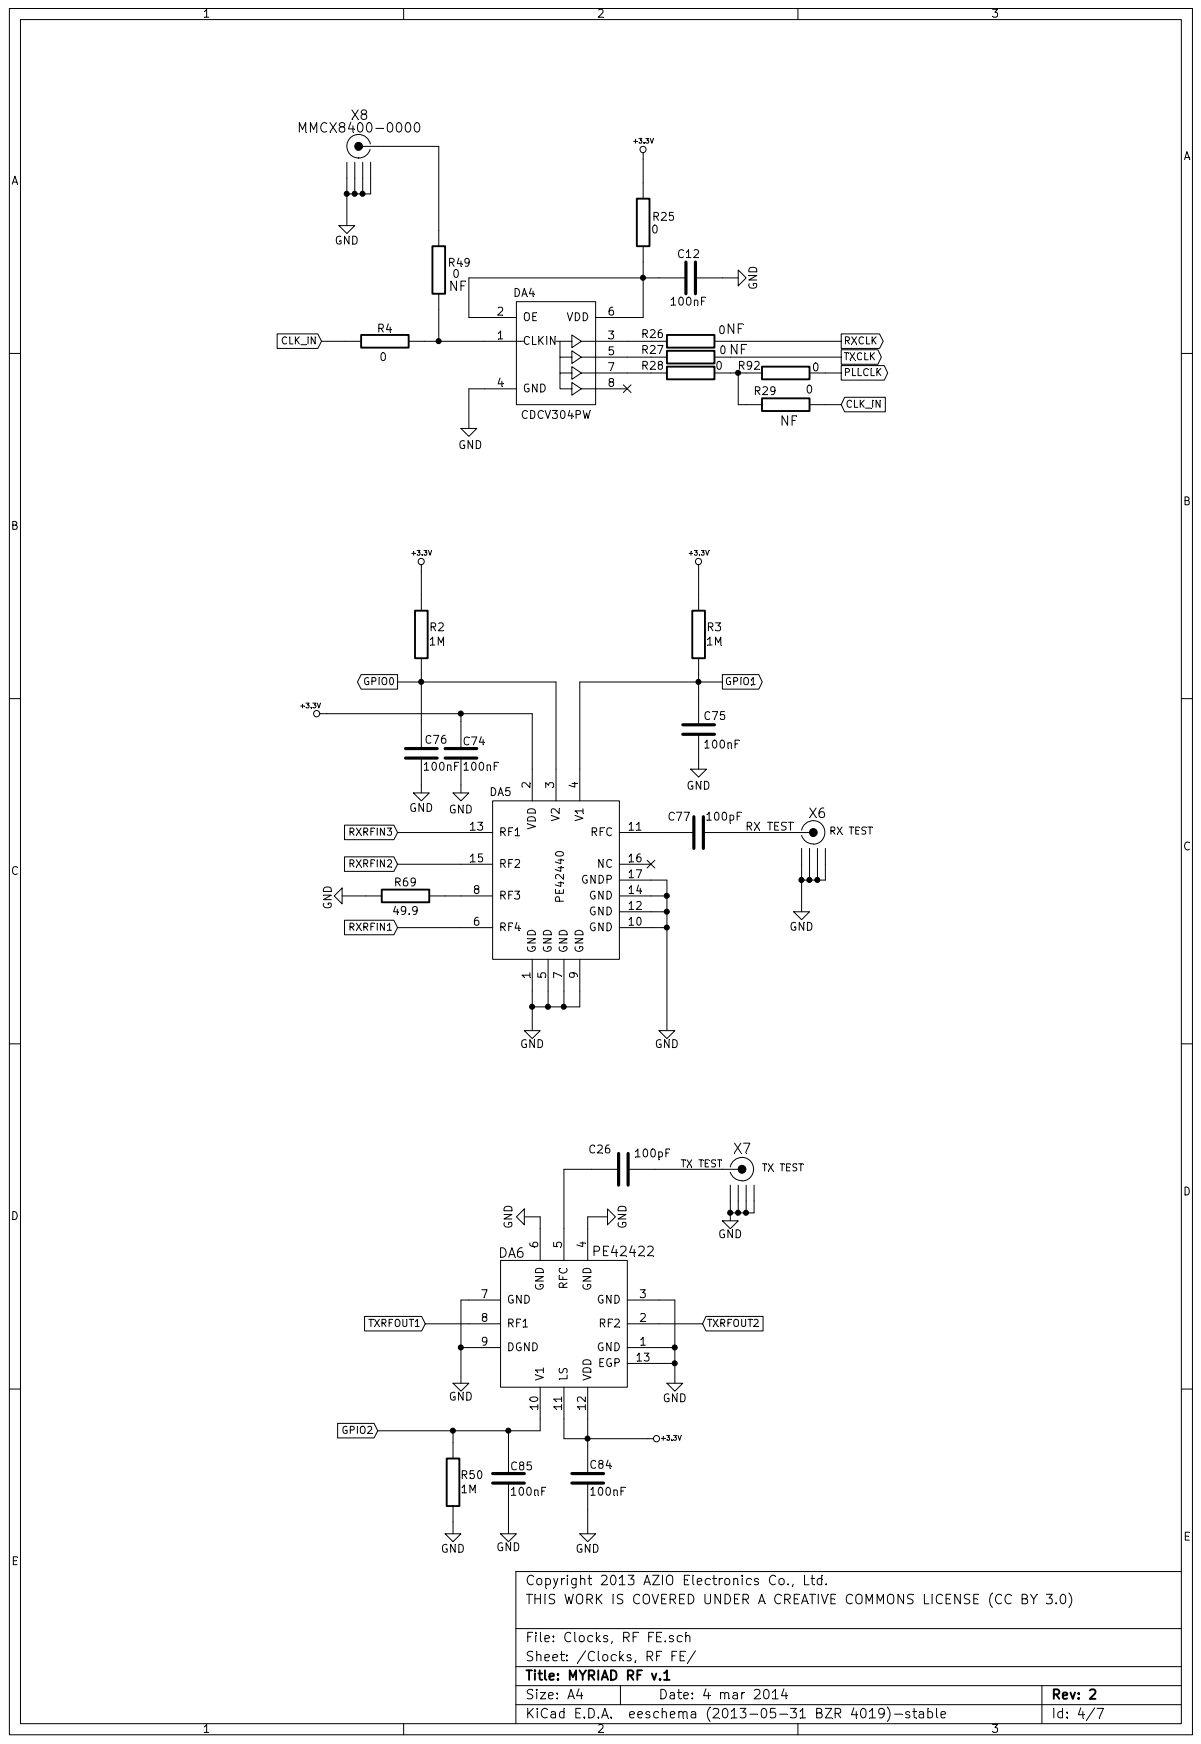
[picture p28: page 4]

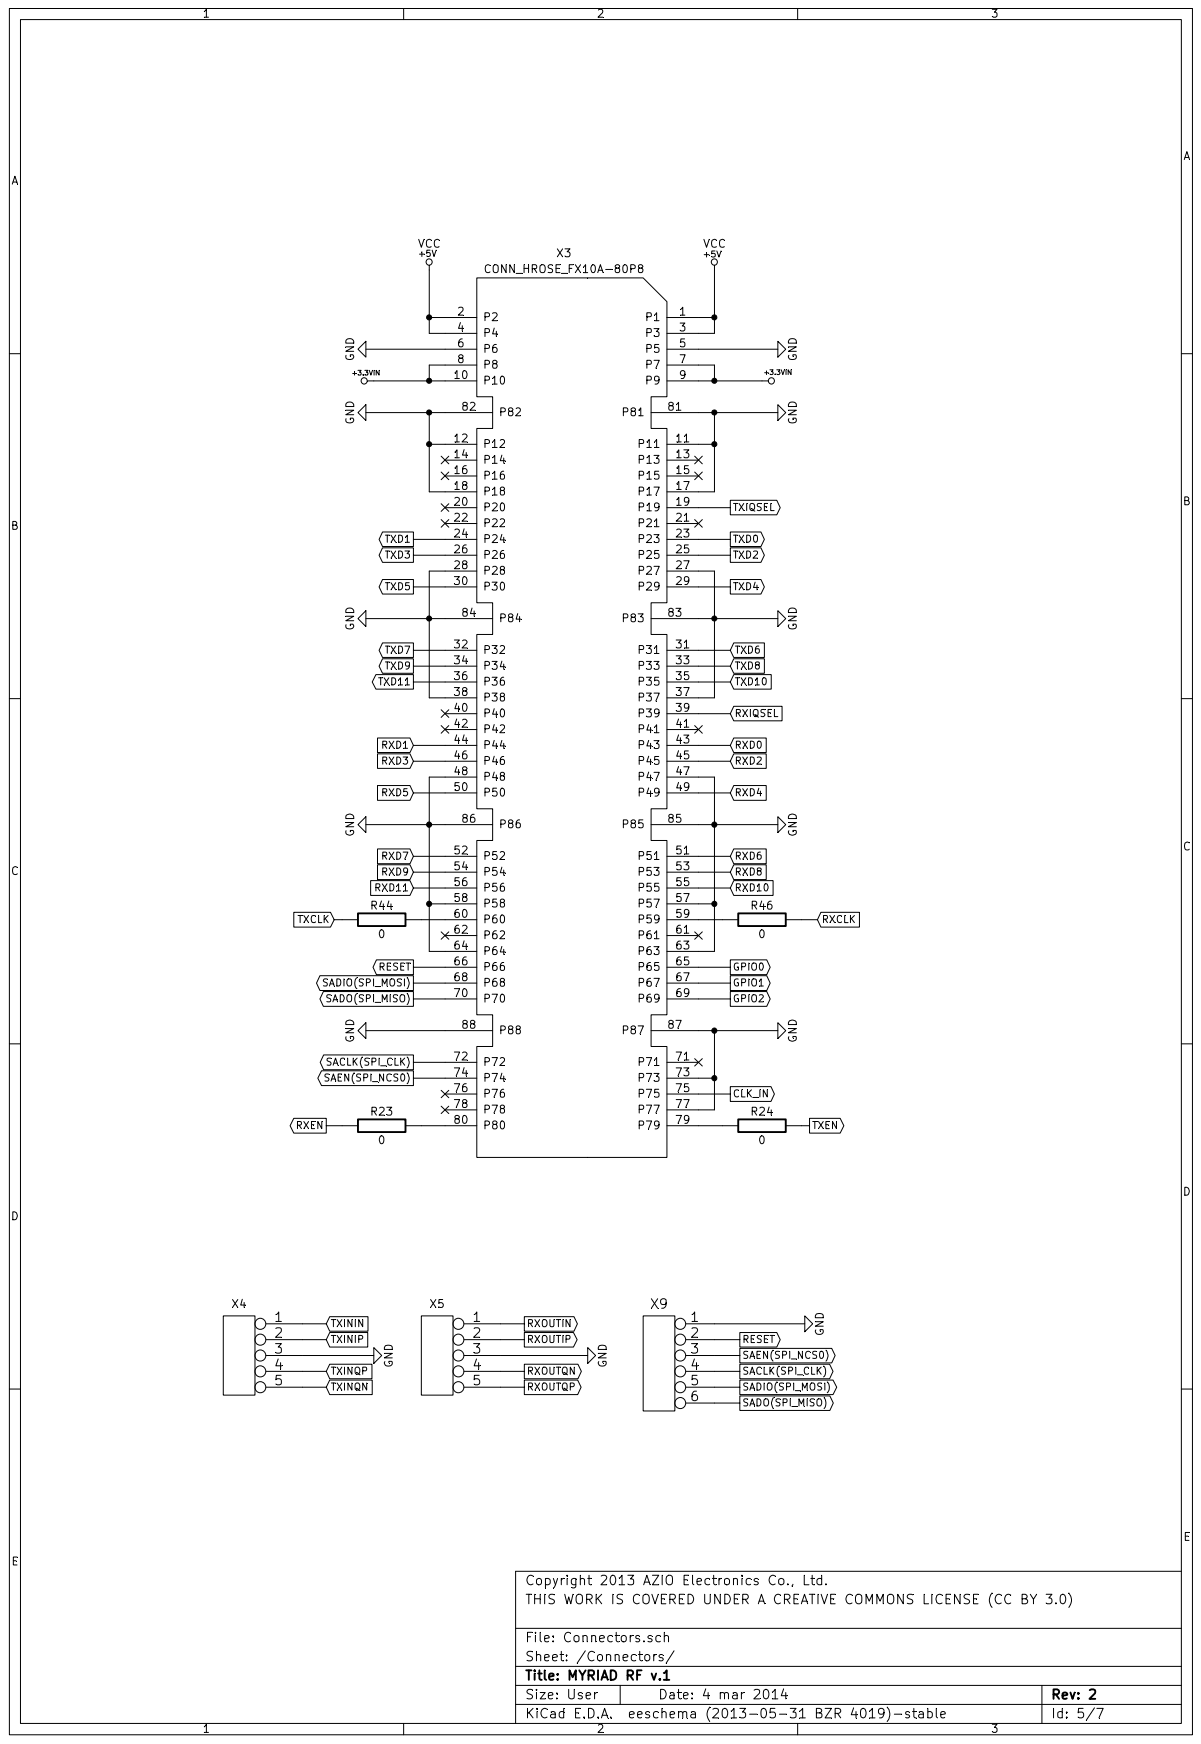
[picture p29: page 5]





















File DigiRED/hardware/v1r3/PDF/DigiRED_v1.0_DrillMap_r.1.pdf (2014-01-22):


C:\DigiRED_v.1_r.1\Gerbers.bin L5: DigiRED_v1-drl_map.pho (SIG)

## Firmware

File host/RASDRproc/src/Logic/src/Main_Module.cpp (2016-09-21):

// -----------------------------------------------------------------------------
// FILE: 		Main_Module.cpp
// DESCRIPTION:
// DATE:		2013-05-06
// AUTHOR(s):	Lime Microsystems
// REVISIONS:
// -----------------------------------------------------------------------------

#include "Main_Module.h"
#include "ConnectionManager.h"

#include "TestingModule.h"
#include "CallbackCodes.h"
#include "Board2_Module.h"
#include "ADF_Module.h"
#include "TimeCOunter.h"

#ifdef WIN32
    #include <windows.h>
    #include <dbt.h>
	HINSTANCE hinst;
	HWND hwnd;
	DWORD threadID;
	HANDLE threadHandle;
#endif
// ---------------------------------------------------------------------
using namespace std;

GUID allGUIDs = {0xA5DCBF10L, 0x6530, 0x11D2, {0x90, 0x1F, 0x00, 0xC0, 0x4F, 0xB9, 0x51, 0xED}};

Main_Module* Main_Module::g_pMain = NULL;

/**
	Creates thread that runs Windows message loop. It is needed
	to be able to detect chip connection and disconnection.
*/
int Main_Module::StartMessagePump()
{
#ifdef WIN32
	threadHandle = CreateThread(NULL, 0, WinMessagePump, NULL, 0, &threadID);
	if (threadID == NULL)
    {
		return 0;
    }
#endif
	return 1;
}

/**
	Stops windows message loop thread.
*/
int Main_Module::StopMessagePump()
{
    #ifdef WIN32
	if(threadID != NULL)
	{
		CloseHandle(threadHandle);
		return 1;
	}
	#endif
	return 0;
}

/**
	Processes Windows messages, reacts to device changes.
*/
#ifdef WIN32
LRESULT CALLBACK Main_Module::WndProc (HWND hwnd, UINT message, WPARAM wParam, LPARAM lParam)
{
    switch (message)
    {
    case WM_DESTROY:
        PostQuitMessage (0);
        return 0;
    case WM_DEVICECHANGE:
        PDEV_BROADCAST_HDR pHdr = (PDEV_BROADCAST_HDR)lParam;
        string devname;
        string stemp;
        bool chipEvent = false;
        if(pHdr)
        {
            switch( pHdr->dbch_devicetype )
            {
                //check if device pid and vid matches chip
                case DBT_DEVTYP_DEVICEINTERFACE:
                    PDEV_BROADCAST_DEVICEINTERFACE pDevInf = (PDEV_BROADCAST_DEVICEINTERFACE)pHdr;
                    devname = pDevInf->dbcc_name;
                    int p1 = devname.find_first_of('#');
                    if(p1 != string::npos )
                        ++p1;
                    stemp = devname.substr(p1, 4);
                    transform(stemp.begin(), stemp.end(),stemp.begin(), ::toupper);
                    if(stemp == "VID_")
                    {
                        stemp = devname.substr(p1+4, 4);
                        transform(stemp.begin(), stemp.end(),stemp.begin(), ::toupper);
                        if(stemp == "04B4")
                            chipEvent = true;
                        else
                            break;
                    }
                    stemp = devname.substr(p1+9, 4);
                    transform(stemp.begin(), stemp.end(),stemp.begin(), ::toupper);
                    if(stemp == "PID_")
                    {
                        stemp = devname.substr(p1+13, 4);
                        transform(stemp.begin(), stemp.end(),stemp.begin(), ::toupper);
                        if(stemp == "00F1")
                            chipEvent = true;
                        else
                            break;
                    }
                    if(chipEvent)
                    {
                        g_pMain->getTesting()->StopSdramRead();
                        g_pMain->getSerPort()->DevicesChanged();
                    }
                    break;
            }
        }
        break;
    }
    return DefWindowProc (hwnd, message, wParam, lParam);
}
#endif

/**
	Creates invisible window to receive Windows messages and runs Windows messages loop
*/
#ifdef WIN32
DWORD WINAPI Main_Module::WinMessagePump(void *param)
{
	MSG msg;
	WNDCLASS wc;
    HANDLE hInstance = GetModuleHandle(NULL);
    wc.style = 0;                                   // Class style
    wc.lpfnWndProc = (WNDPROC) WndProc;             // Window procedure address
    wc.cbClsExtra = 0;                              // Class extra bytes
    wc.cbWndExtra = 0;                              // Window extra bytes
    wc.hInstance = (HINSTANCE)hInstance;            // Instance handle
    wc.hIcon = LoadIcon (NULL, IDI_WINLOGO);        // Icon handle
    wc.hCursor = LoadCursor (NULL, IDC_ARROW);      // Cursor handle
    wc.hbrBackground = (HBRUSH) (COLOR_WINDOW + 1); // Background color
    wc.lpszMenuName = NULL;                         // Menu name
    wc.lpszClassName = "MyWndClass";                // WNDCLASS name

    if( !RegisterClass (&wc) )
        cout << "problems registering hidden window" << endl;

	hwnd = CreateWindow (
               "MyWndClass",               // WNDCLASS name
               "InvisibleWindowForNotifications",      // Window title
               WS_DISABLED,                // Window style
               CW_USEDEFAULT,              // Horizontal position
               CW_USEDEFAULT,              // Vertical position
               CW_USEDEFAULT,              // Initial width
               CW_USEDEFAULT,              // Initial height
               //HWND_DESKTOP,               // Handle of parent window
               NULL,               // Handle of parent window
               NULL,                       // Menu handle
               NULL,                       // Application's instance handle
               NULL                        // Window-creation data
           );

	UpdateWindow (hwnd);

	//register device guid for notifications
    DEV_BROADCAST_DEVICEINTERFACE NotificationFilter;

    ZeroMemory( &NotificationFilter, sizeof(NotificationFilter) );
    NotificationFilter.dbcc_size = sizeof(DEV_BROADCAST_DEVICEINTERFACE);
    NotificationFilter.dbcc_devicetype = DBT_DEVTYP_DEVICEINTERFACE;
    NotificationFilter.dbcc_classguid = allGUIDs;

    HDEVNOTIFY hDeviceNotify = RegisterDeviceNotification(
        hwnd,                       // events recipient
        &NotificationFilter,        // type of device
        DEVICE_NOTIFY_WINDOW_HANDLE // type of recipient handle
        );

    BOOL bRet;
    while( (bRet = GetMessage( &msg, NULL, 0, 0 )) != 0)
    {
        if (bRet == -1)
        {
            // handle the error and possibly exit
        }
        else
        {
			TranslateMessage(&msg);
            DispatchMessage(&msg);
        }
    }
    // Return the exit code to the system.
    return msg.wParam;
}
#endif

/**
	Initializes main module variables and callback function pointers.
*/
Main_Module::Main_Module()
{
    m_initialized = false;
	g_pMain = this;
	m_RefClk = 0;

	sbMain[1] = " Automatic Download Mode";
	updateInterfaceCallback = NULL;

	m_TopModule = NULL;
	m_RxLpfModule = NULL;
	m_TxLpfModule = NULL;
	m_TxRfModule = NULL;
	m_RxVga2Module = NULL;
	m_RxFeModule = NULL;
	m_TxPLLModule = NULL;
	m_RxPLLModule = NULL;
	m_ADDCModule = NULL;
	m_Board2Module = NULL;
	m_ADFModule = NULL;
	m_serPort = new ConnectionManager(this);
	if (!m_serPort->IsOpen())
	{
		autoDownload = false;
		slLogMesg(SERIAL_PORT_NOT_ACCESSABLE);
	}
	else
	{
		autoDownload = true;
		slLogMesg(SERIAL_PORT_INITIALIZED);
	};


	m_iRefVCnt = 3;
	m_dFVco1 = new double[m_iRefVCnt];
	m_dFVco2 = new double[m_iRefVCnt];
	m_dFVco3 = new double[m_iRefVCnt];
	m_dFVco4 = new double[m_iRefVCnt];
	m_iCVco1 = new int[m_iRefVCnt];
	m_iCVco2 = new int[m_iRefVCnt];
	m_iCVco3 = new int[m_iRefVCnt];
	m_iCVco4 = new int[m_iRefVCnt];
	memset(m_dFVco1, 0, sizeof(double)*m_iRefVCnt);
	memset(m_dFVco2, 0, sizeof(double)*m_iRefVCnt);
	memset(m_dFVco3, 0, sizeof(double)*m_iRefVCnt);
	memset(m_dFVco4, 0, sizeof(double)*m_iRefVCnt);

	// For interprocess communication
	m_sInterPD.iLen = 1;
	m_sInterPD.cCmdW = new char[m_sInterPD.iLen];
	m_sInterPD.cDataW = new char[m_sInterPD.iLen];
	m_sInterPD.cCmdR = new char[m_sInterPD.iLen];
	m_sInterPD.cDataR = new char[m_sInterPD.iLen];
	m_sInterPD.iRInd = new int[m_sInterPD.iLen];
	m_sInterPD.iWInd = new int[m_sInterPD.iLen];
	memset(m_sInterPD.cCmdW, 0, m_sInterPD.iLen);
	memset(m_sInterPD.cDataW, 0, m_sInterPD.iLen);
	memset(m_sInterPD.cCmdR, 0, m_sInterPD.iLen);
	memset(m_sInterPD.cDataR, 0, m_sInterPD.iLen);
	memset(m_sInterPD.iRInd, 0, m_sInterPD.iLen*sizeof(int));
	memset(m_sInterPD.iWInd, 0, m_sInterPD.iLen*sizeof(int));
	m_sInterPD.iToR = m_sInterPD.iLen;
	m_sInterPD.iToW = m_sInterPD.iLen;

	sbMain[1] = " Automatic Download Mode";
	sbMain[2] = " Ref. Clock, Hz: 40000000";

	m_ver = 0;
	m_rev = 0;
	m_mask = 0;
}

/**
	Deletes dynamic variables and stop windows message loop.
*/
Main_Module::~Main_Module()
{
	g_pMain = NULL;

	delete[]m_sInterPD.cCmdW;
	delete[]m_sInterPD.cDataW;
	delete[]m_sInterPD.cCmdR;
	delete[]m_sInterPD.cDataR;
	delete[]m_sInterPD.iRInd;
	delete[]m_sInterPD.iWInd;

	delete[]m_dFVco1;
	delete[]m_dFVco2;
	delete[]m_dFVco3;
	delete[]m_dFVco4;

	delete[]m_iCVco1;
	delete[]m_iCVco2;
	delete[]m_iCVco3;
	delete[]m_iCVco4;

	StopMessagePump();
}

/**
	Creates new project file and sets configuration to default values.
*/
void Main_Module::FileNewExecute()
{
	setCurrentFileName("untitled.prj");

	m_TopModule->SetDefaults();
	m_TxLpfModule->SetDefaults();
	m_RxLpfModule->SetDefaults();
	m_TxRfModule->SetDefaults();
	m_RxVga2Module->SetDefaults();
	m_RxFeModule->SetDefaults();
	m_TxPLLModule->SetDefaults();
	m_RxPLLModule->SetDefaults();
	m_ADDCModule->SetDefaults();
	//m_BoardModule->SetDefaults();

	LoadAdditionalSettings();

	slLogMesg(PROJECT_FILE_CREATED);
}

/**
	Checks if given file is not empty.
*/
bool Main_Module::FileIsNotEmpty(string filename)
{
	long length;
	FILE *stream;

	stream = fopen(filename.c_str(), "r");

	fseek(stream, 0L, SEEK_END);
	length = ftell(stream);
	fclose(stream);

	return (length > 0);
}

/**
	Loads configuration settings from file.
*/
void Main_Module::LoadConfiguration(string sIniName)
{
	ini_t *ini;
	ini = new ini_t(sIniName); // we will serialize the data from the file
	ini->Parse();

	m_UARFCNDef.ReadConf(ini);
	m_TopModule->ReadConf(ini);
	m_TxLpfModule->ReadConf(ini);
	m_RxLpfModule->ReadConf(ini);
	m_TxRfModule->ReadConf(ini);
	m_RxVga2Module->ReadConf(ini);
	m_RxFeModule->ReadConf(ini);
	m_TxPLLModule->ReadConf(ini);
	m_RxPLLModule->ReadConf(ini);
	m_ADDCModule->ReadConf(ini);

	m_RefClk = m_TxPLLModule->GetRefClk();

	delete ini;

	slLogMesg(PROJECT_FILE_OPENED);
};

/**
	Loads given configuration file and send configuration to the chip.
	@param filename filename or full path to file.
*/
void Main_Module::FileOpenExecute(string filename)
{
	setCurrentFileName(filename);
	LoadConfiguration(filename);
	slLogMesg(PROJECT_FILE_OPENED);

	Download();
}

/**
	Enables all SPI clocks in Top SPI.
*/
void Main_Module::EnableAllSPIClocks()
{
	// Enable all SPI clocks in TopSPI
	m_TopModule->EnableAllSPIClocks();
	m_serPort->SPI_Write(m_TopModule->GetPrData());
	milSleep(5);
};

/**
	Restores all SPI clocks in Top SPI.
*/
void Main_Module::RestoreAllSPIClocks()
{
	// Enable all SPI clocks in TopSPI
	m_TopModule->RestoreAllSPIClocks();
	m_serPort->SPI_Write(m_TopModule->GetPrData());
	milSleep(5);
};
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

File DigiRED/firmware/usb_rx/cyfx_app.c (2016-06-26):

/*
 ## Cypress USB 3.0 Platform source file (cyfxslfifosync.c)
 ## ===========================
 ##
 ##  Copyright Cypress Semiconductor Corporation, 2010-2014,
 ##  All Rights Reserved
 ##
 ##  Use of this file is governed
 ##  by the license agreement included in the file
 ##
 ##     <install>/license/license.txt
 ##
 ##  where <install> is the Cypress software
 ##  installation root directory path.
 ##
 ##  Published with permission, Case #2427983098, Cypress Semiconductor Corp.
 ##
 ##  This source code is derived from the Cypress EZ-USB SDK Example:
 ##  'Slave FIFO Synchronous Mode'.  As per clause 1.1 of the above license,
 ##  it is a derivative work of The Society of Amateur Radio Astronomers,
 ##  who retain copyright, all rights reserved.  The modifications to the
 ##  example that are made by the Society of Amateur Radio Astronomers, are
 ##  in turn made available to you under the GNU Public License, Version 2.
 ##
 ##  You should have received a copy of the GNU General Public License
 ##  along with this source code; see the file COPYING.  If not, write to
 ##  the Free Software Foundation, Inc., 51 Franklin Street,
 ##  Boston, MA 02110-1301, USA.
 ##  
 ##  This entire code is distributed in the hope that it will be useful but
 ##  WITHOUT ANY WARRANTY. ALL WARRANTIES, EXPRESS OR IMPLIED ARE HEREBY
 ##  DISCLAIMED. This includes but is not limited to warranties of
 ##  MERCHANTABILITY or FITNESS FOR A PARTICULAR PURPOSE.
 ##
 ## ===========================
*/

/* This file illustrates the Slave FIFO Synchronous mode example */

/*
   This interface comprises of two USB bulk endpoints. A bulk OUT endpoint
   acts as the producer of data from the host. A bulk IN endpoint acts as
   the consumer of data to the host. Appropriate vendor class USB enumeration
   descriptors with these two bulk endpoints are implemented.

   The GPIF configuration data for the Synchronous Slave FIFO operation is loaded onto
   the appropriate GPIF registers. The p-port data transfers are done via the producer
   p-port socket and the consumer p-port socket.

   This application implements two DMA Channels in MANUAL mode one for P to U data transfer
   and one for U to P data transfer.

   The U to P DMA channel connects the USB producer (OUT) endpoint to the CPU
   socket. The P to U DMA channel connects the producer p-port socket to the USB 
   consumer (IN) endpoint.

   CPU is signaled of the data reception using DMA callbacks. The CPU
   discards this buffer. This leads to the sink mechanism. A callback is raised whenever
   a buffer is available on the producer p-port socket.  The CPU commits this to 
   the DMA data transfer to the consumer endpoint which then gets transferred to the host.

   Upon every reception of data in the DMA buffer from the host or from the p-port, the
   CPU is signalled using DMA callbacks. There are two DMA callback functions implemented
   each for U to P and P to U data paths. The CPU then commits the DMA buffer received so
   that the data is transferred to the consumer.

   The DMA buffer size for each channel is defined based on the USB speed. 64
   for full speed, 512 for high speed and 1K for super speed. The number of
   DMA buffers is defined by CY_FX_DMA_BUF_COUNT.

   The firmware implements vendor commands 0xC0 and 0xC1 on control EP0
   to perform programmed I/O read or write firmware operations, respectively.
   All firmware transactions are performed as a sequence of 0xC1 (WRITE, CMD)
   followed by a 0xC0 (READ STATUS).  The 0xC0 allows the host to obtain the
   result of the 0xC1 command or the data requested by it.  Refer to the
   RASDR API document for details on the available functions and return codes.
  */
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

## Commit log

2013-10-08 Added de0-Nano interface firmware
    [Clock Generator.sch, Data Interface Connector.sch, DigitalInterface_v1.0-Back.gbl, DigitalInterface_v1.0-Front.gtl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]
2013-10-31 Initial commit of the Zipper interface design files
    [ADF4002.sch, Buffers.sch, Clock Generator.sch, Data Interface Connector.sch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]
2014-01-22 Initil commit of hardware design
    [Clock Generator.sch, Connectors.sch, DigiRED_v1.0-B_Mask.gbs, DigiRED_v1.0-B_Paste.gbp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]
2014-02-27 Updated dev kit PDF, and hardware design for placement error
    [ADF4002.sch, Buffers.sch, Clock Generator.sch, Data Interface Connector.sch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]
2014-03-05 Updated PCB database
    - Schematics updates, pages "Clocks” and “RF FE":
    1. Component DA6 - Obsolete RF switch (PE4210) is changed, to new part
    PE42422
    2. Added capacitor on TX Test track C26=100pF
    - PCB Layout updates:
    1. New footprint of PE42422 part
    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
    [Analog Circuits.sch, Clocks, RF FE.sch, Connectors.sch, Digital Circuits.sch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]
2014-03-07 Added VIA_IN_PAD version of updated RF module design and archived old versions
    [Analog Circuits.sch, Clocks, RF FE.sch, Connectors.sch, Digital Circuits.sch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]
2014-04-23 initial revision of plotcsv, processing RASDRviewer_W_1_0_4 FFTOut.csv files
    [FFTOut-datetime.csv, FFTOut-example.csv]
2014-05-12 refactored to handle datetime as core instead of excel-datetime; allow array or line processing; add logging module; add background subtraction capability
    [FFTOut-example.csv]
2014-05-16 plotcsv program to go with RASDRviewer 1.0.5.x
    [FFTOut-datetime.csv, FFTOut-general.csv]
2014-06-02 add initial case design collateral
    [rasdr2-case-bottom.scad, rasdr2-case-mfg.scad, rasdr2-case-mfg.stl, rasdr2-case-top.scad]
2014-12-16 Added RFDIO connector specification
2015-01-29 re-arrange files in preparation for merge to RASDR/master
    [ADF4002.sch, Analog Circuits.sch, Buffers.sch, Clock Generator.sch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]
2015-01-29 ECO 1: change 6 0.1mm vias to 0.2mm, update BOM
    [MYRIAD_RF-B_Cu.gbl, MYRIAD_RF-B_Mask.gbs, MYRIAD_RF-B_Paste.gbp, MYRIAD_RF-B_SilkS.gbo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]
2015-03-11 define one plating spec., update BOM
    + ensure only one electroplating specification is applied
    + depopulate all components in support of the TX FX3 chip
    + ensure +5V power is obtained from external interface only
    to prevent USB current backflow and possible damage to host controllers.
    [DigiRED_v1.0_BOM.xls]
2015-03-11 fit R135 to enable output on Pluto+ oscillator
    [DigiRED_v1.0_BOM.xls]
2015-03-14 adjust BOM for updates parts following CM review
    + change oscillator to CTS/Valpey which has a shorter lead time (10wks)
    + change end-launch SMA connectors to enable bulkhead mount
    + update source for Si5356A-B to Mouser who has stock
    + update replacement parts according to CM review
    [DigiRED_v1.0_BOM.xls, MYRIAD_RF_BOM.xls]
2015-03-14 behavior reference of DigiRED+MyriadRF combinations performed July 2014
    [tables.xlsx]
2015-04-04 update case design for first prototype/production
    + use correct cutout pattern for RR-MSBFPM-06GR
    + add vent slots on side of case
    + add nuts for small rubber foot
    + add slot to view status/activity LEDs on front
2015-04-05 rename Gerber output filenames to match KiCAD output
    NOTE: I was *not* able to successfully figure out how to make KiCAD name
    the files to what I wanted; it seems to have a mind of its own. Any help
    here is appreciated.
    [DigiRED_v1.0-B_Cu.gbl, DigiRED_v1.0-F_Cu.gtl, DigiRED_v1.0-Inner1_Cu.gbr, DigiRED_v1.0-Inner2_Cu.gbr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]
2015-04-08 update mounting screw and vents per Protocase, add dimensioned drawing of first article
2015-04-09 re-export the archived design to gerbers and document how to compare output
    [DigiRED_v1.0-B_Cu.gbl, DigiRED_v1.0-B_Mask.gbs, DigiRED_v1.0-B_Paste.gbp, DigiRED_v1.0-B_SilkS.gbo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]
2015-04-28 adjust REFCLK hole and label down by 1/32 for better fit
2015-05-10 update for processing the various formats from 1.0.4, 1.1.1 and 1.2.2
    [FFTOut-format-1.0.4-localtime.csv, FFTOut-format-1.0.4-universaltime.csv, FFTout-format-1.1.1-localtime.csv, FFTout-format-1.1.1-universaltime.csv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]
2015-05-30 handle degenerate cases of less than 2 records better
    - add missing background file referenced in test.bat from last commit
    - add additional test cases to handle 'self' background as test file
    - add additional test cases to handle plot of background waveform
    [FFTOut-format-1.2.2-background.csv]
2015-06-13 fix broken link on top-level, add montage w/case and userguide
2015-06-13 update specs to match diagram and LMS6002D datasheet, update dimentions to reference the case
2015-06-18 add manufacturing files for RASDR along with BOM and cost projections
    [DigiRED_v1-01-Front_Cu.gtl, DigiRED_v1-02-GND_Cu.gbr, DigiRED_v1-03-Signal_1_Cu.gbr, DigiRED_v1-04-Signal_2_Cu.gbr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]
2015-06-18 image for pacifier needed on some myriadrf boards
2015-06-18 oops, add missing case design image
2015-06-27 add cost of oscillator and synthesizer to BOM
    they were not quoted in Advanced Assembly's due to MOQ issue
    [rasdr2-bom-and-components.xlsx]
2015-10-08 update with current parameters and help
2015-10-08 result of re-generating outputs; sync mfg readme order with digired
    [MYRIAD_RF.drl]
2015-10-09 update to current options
2015-12-16 normalize LED handling
2016-01-19 moved RASDRviewer source to RASDRproc
    + fix issues with filename in POWER and FFT output handling
    + add background subtraction support
    + produce .csv file with ongoing statistics
    Provided to David Fields for personal use on September 7, 2015
2016-01-19 fix POWER and FFT file handling once and for all
2016-01-28 fix append mode on FFT and PWR
    + make all timestamps ISO and with millisecond resolution
    + additional notes on hardcoded 16384 that needs to be refactored
    + updated splash screen
    - oops, just noticed I introduced a regression on saving the filename...
2016-02-11 fix POWER out browse not allowing to use the selected file
2016-02-11 correctly identify behavior of POWER output recording
2016-02-14 updated to drivers sent to Paul Oxley on his support case with Cypress on Jan 14, 2016
2016-03-10 start on v2 modifications
    [Clock Generator.sch, Connectors.sch, DigiRED.kicad_pcb, DigiRED.sch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]
2016-05-25 add raw2iq framework/example as a template
2016-06-26 adjust fault LED blink pattern
2016-06-26 add display buffer thread safety and suppress crash on UI mis-handling (temporarily)
2016-06-26 add USB device re-init code
2016-06-28 workaround for NULL endpoint @start, device selection fault
2016-06-28 add IQ offset control, Pwr plot and UI adjustments
    + Added Performance Parameters->Tuning Parameters
    - Removed Pulsar-related UI items (code is Paul Oxleys and is a
    work-in-progress)
    + Adjust window sizes for better visibility
    + Fix Power Plot scaling behavior (it annoyed me greatly)
    + Stop rescaling the Frequency plot each time you start
2016-06-28 simplify distribution to just have one .csv file example and a more useful batch file
    [FFTOut-2msps-500avg-srh77ca.csv]
2016-06-29 fix Power plot scaling
    + nearly a complete re-write of the scaling code
    + handles scaling, buffer crossings, changes in span
    + handles the end of buffer (86400s) properly
    + separate autoscale for time and power axis allows inspection of data
    = remove Display Time popup as it did not have a purpose
    (it may be used in the future to define the buffer size (86400s) etc.
    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
2016-07-23 add socket and RSS-integration control variables
2016-07-24 add code to serve a TCP/IP socket using the RSS protocol
    The basic principle is to spawn a thread in parallel to the read data
    thread. This thread will setup a socket server, accept inbound
    connections and serve the protocol as described by:
    http://cygnusa.blogspot.com/2015/07/how-to-talk-to-radio-sky-spectrograph.html
    The thread will read from a circular buffer provided by the m_fftAvgFIFO.
    This FIFO is written from the GUI by the function
    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
2016-08-04 add rss-test.py script framework
2016-08-04 implement 1st cut
2016-08-04 add timestamps and rtl-power fields; keep output to 80 col
2016-08-30 implement a more consistently successful recovery
    + add ResetEndpoint
    + threadsafe ConnectionManager
    + use manual reset event for event wait object
    + eliminate length getting changed by reference
    + some additional notes
    Some pork-barrel edits:
    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
2016-09-21 compact chip rev and add board serial number
2016-09-26 fix PWR integration timescale when not 1s; disable sample rate change when running
2016-10-18 add notes on using a noise source to calibrate
2016-11-06 add spur observations to go along with issue #14
    [rasdr2-spur-observations.xlsx]
2016-11-29 add shell test case (for running tests on MacOS/Linux)
2016-12-28 add rss2rtl-power project for producing rtl-power compatible data files
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
